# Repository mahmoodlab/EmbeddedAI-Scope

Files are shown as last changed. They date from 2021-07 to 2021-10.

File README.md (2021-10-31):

# Embedded AI Scope

*A 3D printed embedded AI-based microscope for pathology diagnosis.*

© This code is made available for non-commercial academic purposes.

*TL;DR: We present a 3D printed microscope coupled with a tiny embedded AI processor for running deep models trained on whole slide images. Tested on lung cancer and head and neck cancer detection and subtyping for both FFPE slides and frozen sections. The proposed setup can be used in low resouce settings where expensive slide scanners, computing equipment and pathology expertise may not be available. The setup can also be used for immidiate diagnosis from frozen sections during surgery.*

### Requirements

The setup of this device requires two small single-board computers (ideally one of which should be specialized for deep learning, such as an Nvidia Jetson Nano). 
Current STLs support an Nvidia Jetson Nano for model inference and a Raspberry Pi for imaging processing. A Raspberry Pi Camera V2 is used for imaging of samples. The STLs support a battery pack at most as large as the Jetson Nano and a 7 inch touch screen, though the specific dimensions of the variable STLs could be changed to accommodate for different setups (for example a larger screen, larger battery packs, or more than one battery pack). 

### Instructions

STL files for 3D printing are in `/stls`. The prints have been tested using a stereolithography (SLA) 3D printer. It is important to note that the battery pack(s) and screen are not specific to the design, as a wide variety of models and parts would provide the necessary functionality. Consequently, the 3D printed parts that house these components would need to be variable and easily modified to fit specific parts, so we include the scripts that generate these parts for customization. See [here](stls/housing_scripts/modifying_housing_stls.md) for details on modifying these STLs.

To build the device,

* Please see [here](stls/assembly_instructions.pdf) for a list of parts and specific assembly instructions with pictures. 
* Also see [assembly video](https://drive.google.com/file/d/1WPFa4IFCZg4AjeARS-ab-TACosYXbkmb/view?usp=sharing) for a very general overview and timelapse of assembly. 
* Ethernet file transfer (if needed) between the Jetson Nano and the Raspberry Pi can be set up in many ways. See [here](stls/ethernet_instructions.md): for details.
* After assembling and setting up the Ethernet connection (if needed), please see [model instructions](docs/README.md) for installing requirements and a toy example.

High-level overview of device structure and setup:

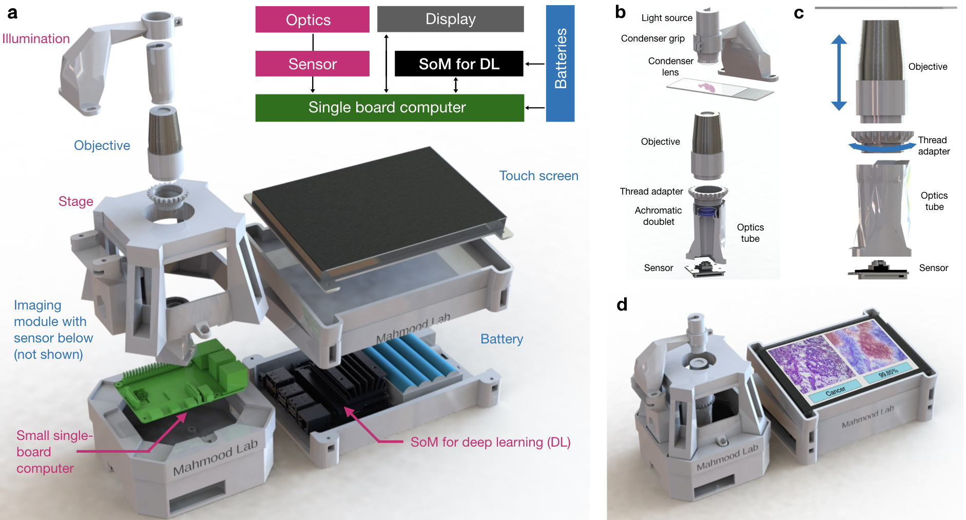
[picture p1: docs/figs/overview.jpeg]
Overview of device


Comparison with traditional development and deployment setups:

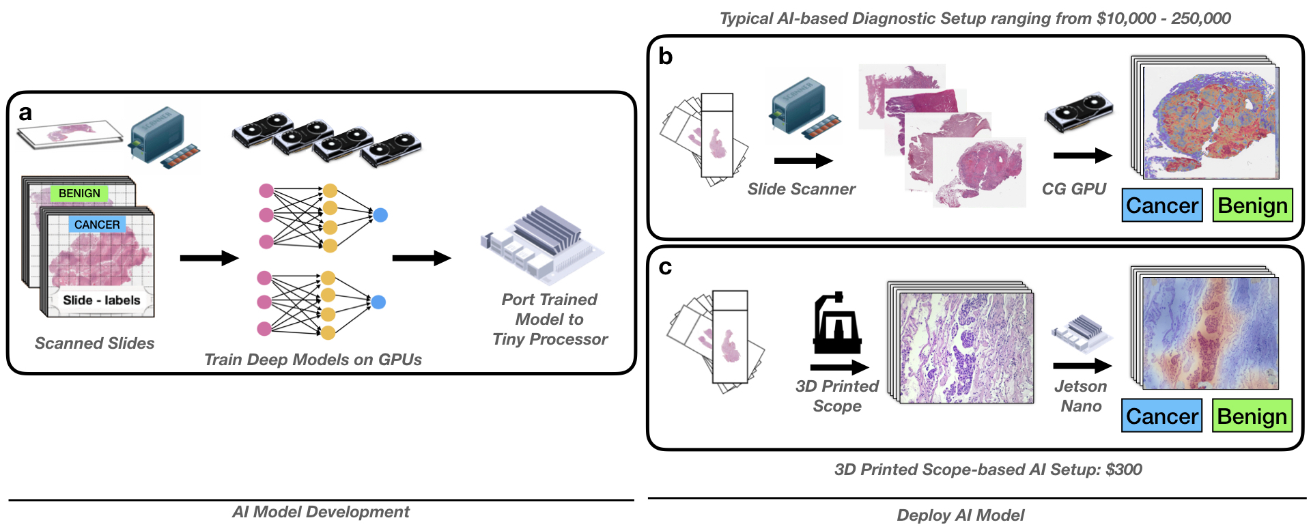
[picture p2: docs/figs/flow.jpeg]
Pipeline flow


### Acknowledgments
[CLAM](https://github.com/mahmoodlab/CLAM) and [OpenFlexture](https://github.com/rwb27/openflexure_microscope)

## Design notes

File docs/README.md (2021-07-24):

### TOY Example
First download [data](https://drive.google.com/drive/folders/1ofAFtL0PJd7fewOs3b44ejUzM-FwyQk0?usp=sharing) and put the data folder bwh_lung_2652 inside **phone_clam/data/**

See [here](INSTALLATION.md) for installation.

To run example:
``` shell
CUDA_VISIBLE_DEVICES=0 python infer_and_interpret.py --config_file heatmap_config_test.yaml --overlap 0.5
```

Generated heatmaps will be saved under **heatmaps/heatmap_production_results**.
Inferred results will be saved under **heatmaps/results**.
Settings can be modified using .yaml config files stored under **heatmaps/configs**; the config file corresponding the toy example is **heatmap_config_test.yaml** and is passed to the inference script via --config_file

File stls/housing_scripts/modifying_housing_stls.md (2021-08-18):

### Modifying STLs for screen, battery, and Jetson housing

The default design consists of a microscope component and a separate deep learning component. The microscope STLs are fixed due to specific dimensions (such as focal lengths and tube lengths) to achieve the desired magnification. However, the deep learning component also houses a touch screen and battery packs, which are up to a high degree of customization specific to a build (such as using different sized battery packs and screens with different dimensions). 

To address this, we provide the openSCAD scripts that generate the STLs and made it modular and easy to customize so that the STLs can be adapted to these highly variable parts.

#### Using openSCAD

The scripts are located in `lcd_and_board.scad`. These scripts generate both the top and bottom half of the housing component. See the comments in the script for details.

#### Other options

Aside from directly modifying openSCAD, these parts were designed with relatively simple transforms in mind so that it is recognizable by CAD software, such as using the Recognize Features function of FeatureWorks as part of SolidWorks).

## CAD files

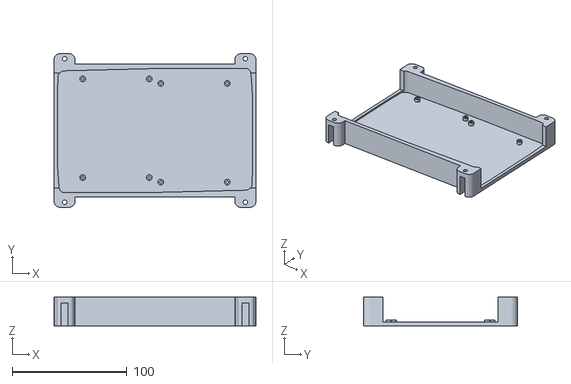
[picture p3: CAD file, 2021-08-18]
stls/lcd_and_board_bottom_part.stl
176.0 x 134.0 x 25.0

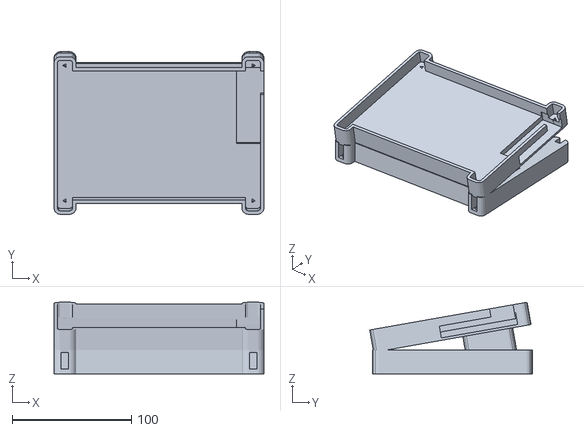
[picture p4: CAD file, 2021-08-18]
stls/lcd_and_board_top_part.stl
176.0 x 136.3 x 60.0

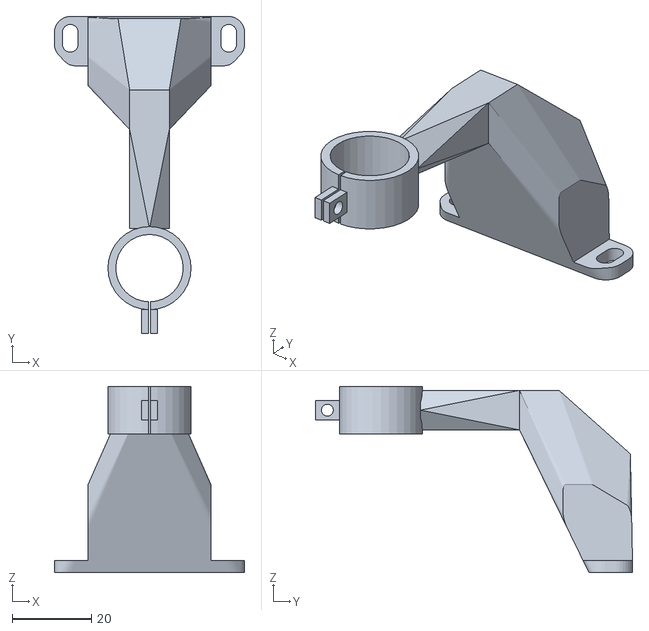
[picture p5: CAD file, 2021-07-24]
stls/condenser_mount.stl
48.0 x 80.0 x 47.0

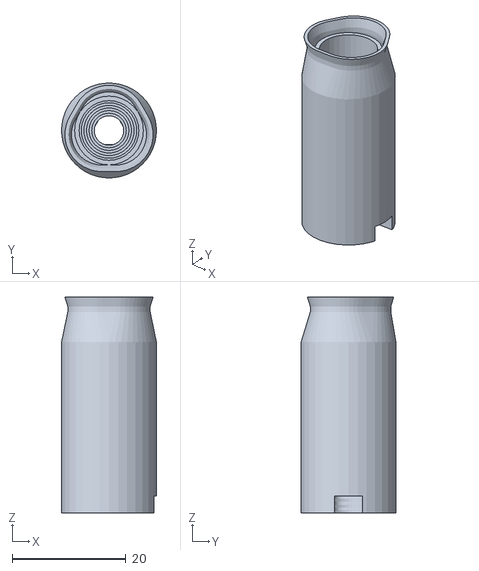
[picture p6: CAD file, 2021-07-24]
stls/condenser.stl
16.7 x 16.7 x 38.0

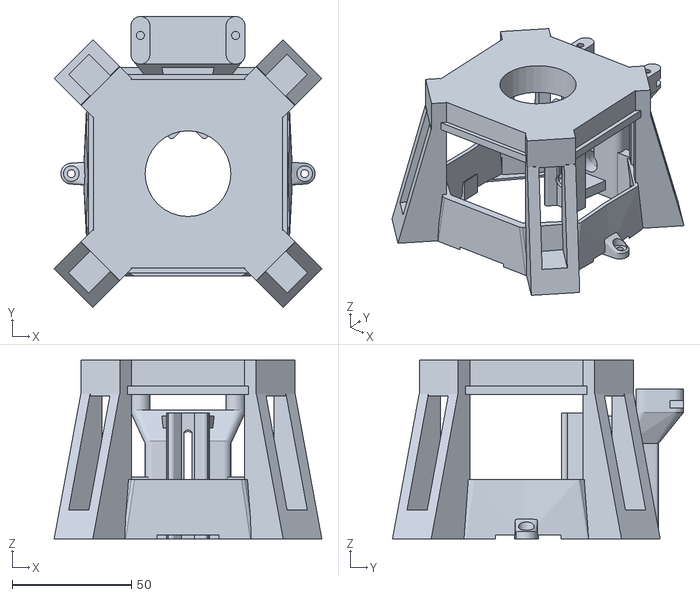
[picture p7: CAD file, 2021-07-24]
stls/stage.stl
112.4 x 122.2 x 75.0

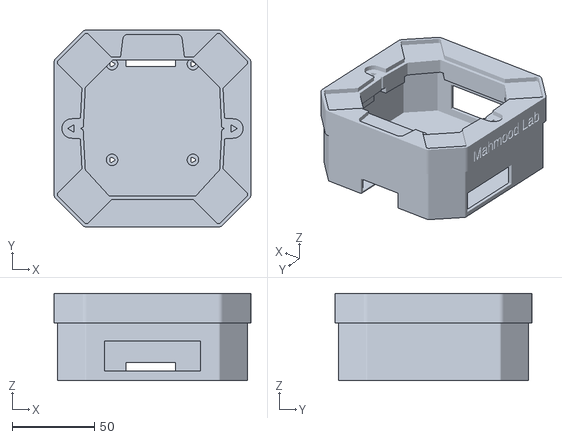
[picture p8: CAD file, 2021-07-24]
stls/microscope_stand.stl
119.4 x 119.4 x 53.0

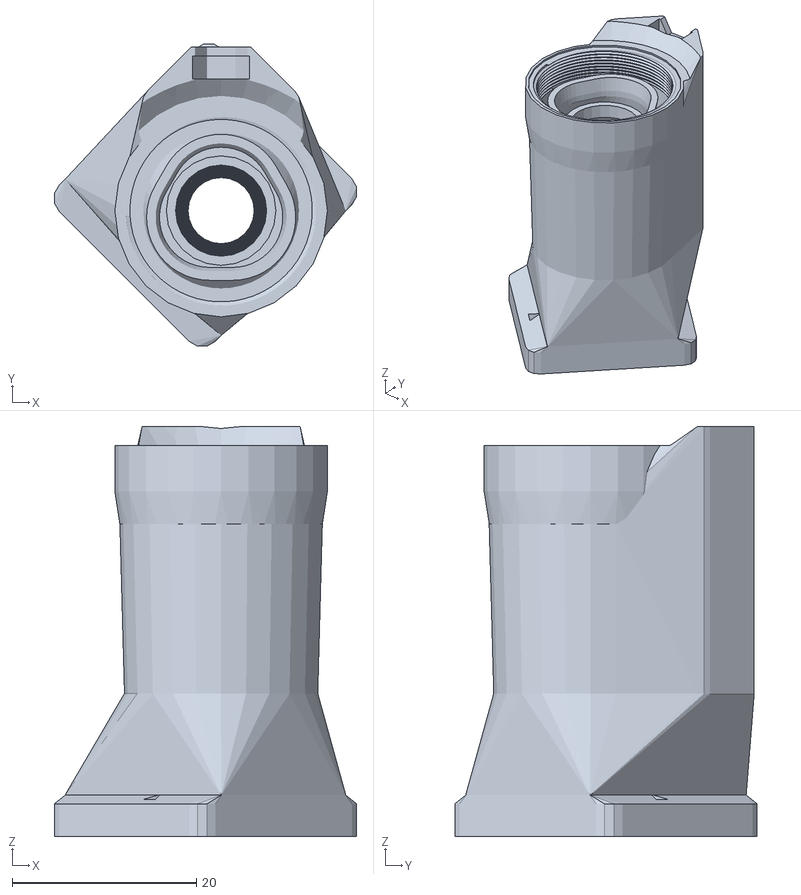
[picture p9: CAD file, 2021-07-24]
stls/optics_thread_tube.stl
32.9 x 32.9 x 44.5

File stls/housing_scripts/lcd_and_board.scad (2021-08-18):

eps = 0.05; // tolerance value 
screen_dims = [166, 106, 12]; // x,y,z dimensions of screen in milimeters, depends on screen
screw_port_dims = [8.5, 9, screen_dims.z]; // x,y,z dimensions of screen screw holes relative to the corner of the screen, depends on screen
board_dims = [];
board_pos1 = [-63,45,5];
board_pos2 = [63,-45,5];

/**
Note that base_height needs to be greater than height of Jetson and height of battery pack(s).
**/
base_height = 45; // Height of base of top housing component measured from bottom
bottom_height = 25; // Height of bottom housing component

// LCD casing is rotated to give a 10 degree slant
LCD_slant = 10;

// Positions of LCD ports to hollow out later
module lcd_screw_ports(screen = screen_dims, screw = screw_port_dims) {
    translate([screen.x/2-screw.x, screen.y/2, 0]) cube(screw_port_dims);
    mirror([1,0,0]) translate([screen.x/2-screw.x, screen.y/2, 0]) cube(screw_port_dims);
}

// Basic structure of screen to hollow out space later
module screen(screen = screen_dims) {
    translate([-screen.x/2, -screen.y/2, 0]) cube(screen);
}

// Make a 2D footprint of the basic LCD screen structure used to offset and extrude later to form outer structure of LCD housing
module lcd_footprint(screen = screen_dims, screw = screw_port_dims) {
    offset(2) projection() union() {
        lcd_screw_ports();
        mirror([0,1,0]) lcd_screw_ports();
        translate([-screen.x/2, -screen.y/2, 0]) cube(screen);
    }
}

// Space for LCD body, depends on screen
module lcd_hollow(screen = screen_dims, screw = screw_port_dims) {
    linear_extrude(height = screen_dims.z) lcd_footprint();
}

// Space for wiring to LCD, depends on screen
module lcd_wiring_hollow(screen = screen_dims, screw = screw_port_dims) {
    lcd_wiring_space = [20+3,65,10]; // Dimension of space to be hollowed, depends on screen and wires
    wiring_z_offset = 17; // Z offset for wiring to give extra space
    // Horizontal opening on the right side for wiring
    translate([screen.x/2-lcd_wiring_space.x+5+eps,-screw.y,screen.z-wiring_z_offset]) cube(lcd_wiring_space);
    // Extra space for bulkier HDMI cord
    translate([screen.x/2+eps,screen.y/2-2*screw.y,screen.z-wiring_z_offset]) cube([5,20,wiring_z_offset]);
}

// Outer structure of LCD housing
module lcd_casing_structure() {
    linear_extrude(height = screen_dims.z + 7) offset(3) lcd_footprint();
}

// Screw holes to secure LCD
module lcd_screw_holes(screen = screen_dims, screw = screw_port_dims) {
    // Holes are defined as with the cylinder function with $fn as 3 so that they are essentially triangular
    lcd_hole_d = 4; // Diameter of LCD screw hole, depends on size of screw used 
    module screw_hole(screen = screen_dims, screw = screw_port_dims) {
        translate([screen_dims.x/2-screw.x/2,screen_dims.y/2+screw.y/2,2]) cylinder(999, d = lcd_hole_d, $fn = 3);
        mirror([1,0,0]) translate([screen_dims.x/2-screw.x/2,screen_dims.y/2+screw.y/2,2]) cylinder(999, d = lcd_hole_d, $fn = 3);
    }
    screw_hole();
    mirror([0,1,0]) screw_hole();
}

// LCD housing to be rotated
module lcd_casing_top() {
    difference() {
        // Outer structure shell for LCD housing
        lcd_casing_structure();
        // Hollow out space for LCD, wiring, and screw ports 
        union() {
            translate([0,0,7+eps]) lcd_hollow();
            translate([0,0,7+eps]) lcd_wiring_hollow();
            lcd_screw_holes();
        }
    }
}

// Rotated LCD housing
module lcd_casing(screen = screen_dims, screw = screw_port_dims) {
    // Rotated to give a slant for ease of usage 
    translate([0,0,(screen.y+2*screw.y+10)*sin(LCD_slant)/2]) rotate(LCD_slant, [1,0,0]) lcd_casing_top();
}

// Two legs to support slanted LCD housing
module lcd_support(screen = screen_dims, screw = screw_port_dims, column_pos = 60) {
    // Make one of the legs
    module lcd_support_column(screen = screen, screw = screw) {
        /**
        The supports are essentially two cylinders hulled together, so support_dims_back and support_dims_front gives the dimensions of the taller and shorter cylinders respectively
        Note these are defined relative to screen and screw ports (this can be changed)
        **/
        support_dims_back = [10,5,(screen.y+2*screw.y+10)*tan(LCD_slant)+1];
        support_dims_front = [10,5,(screen.y+2*screw.y+10)*tan(LCD_slant)/3*2+1];
        // Hull the cylinders together to form the column
        hull() {
            translate([0,(screen.y+2*screw.y+10)*cos(LCD_slant)/2*0.25,-2]) rotate(LCD_slant,[1,0,0]) cylinder(h = support_dims_front.z, r = support_dims_front.y);
            translate([0,(screen.y+2*screw.y+10)*cos(LCD_slant)/2*0.75,-2]) rotate(LCD_slant,[1,0,0]) cylinder(h = support_dims_back.z, r = support_dims_back.y);
        }
    }
    // Make both legs
    leg_pos = 60; // Position of legs
    translate([leg_pos,0,0]) lcd_support_column();
    translate([-leg_pos,0,0]) lcd_support_column();
}

// LCD housing and support 
module lcd_full(screen = screen_dims, screw = screw_port_dims) {
    lcd_casing();
    lcd_support(screen = screen_dims, screw = screw_port_dims);
}

// Model of Jetson Nano used to hollow out space later, quick and easy way to get dimensions and hole positions (could also use cube() or an STL of a different board if needed)
module jetson_space() {
    // Credit to https://grabcad.com/library/jetson-nano-3
    import("./libs/jetson_nano.stl");
}

// The battery pack used in the default setup was originally built as a HAT for Jetosn Nano, so it has the same dimensions and screw hole positions, thus we just repeat the same dimensions and positions twice
module boards(board_pos1, board_pos2) {
    hull() {
        // Change one of these to desired dimensions for custom battery pack(s), leave the other one for Jetson Nano
        translate(board_pos1) rotate(-90, [0,0,1]) jetson_space();
        translate(board_pos2) rotate(90, [0,0,1]) jetson_space();
    }
}

// Hollow out space for board wiring and cords
module board_wiring_cutouts() {
    translate([0,0,15]) cube([999,100,23], center = true);
}

// Hollow out holes for bolt
module hole(screen = screen_dims, screw = screw_port_dims, hole_z, hole_d) {
    translate([screen.x/2-screw.x/2, screen.y/2+screw.y/2+5,hole_z+eps]) cylinder(22, d = hole_d, $fn=25);
}
    
module bottom_base_screw(screen = screen_dims, screw = screw_port_dims) {
    // Define rectangular slot for ease of access to secure bolt and nut
    module slot(screen = screen, screw = screw) { 
        slot_dims = [6,10,base_height-bottom_height];
        translate([screen.x/2-screw.x+slot_dims.x/4,screen.y/2+screw.y/2-slot_dims.y/4+4,-eps]) cube(slot_dims);
    }
    bottom_base_hole_d = 4; // Diameter of hole for bolt
    bottom_base_hole_z = 5; // Height of hole for bolt to hollow out
    // Form slot and holes and reflect to make all four
    union() {
        hole(hole_z = bottom_base_hole_z, hole_d = bottom_base_hole_d);
        slot();
        mirror([1,0,0]) slot();
        mirror([1,0,0]) hole(hole_z = bottom_base_hole_z, hole_d = bottom_base_hole_d);
    }
    mirror([0,1,0]) union() {
        hole(hole_z = bottom_base_hole_z, hole_d = bottom_base_hole_d);
        slot();
        mirror([1,0,0]) slot();
        mirror([1,0,0]) hole(hole_z = bottom_base_hole_z, hole_d = bottom_base_hole_d);
    }
}

// Screw holes to connect top_base and bottom_base together
module top_base_screw(screen = screen_dims, screw = screw_port_dims) {
    top_base_hole_d = 4; // Diameter of hole for bolt
    top_base_hole_z = 15; // Height of hole for bolt to hollow out
    union() {
        hole(hole_z = top_base_hole_z, hole_d = top_base_hole_d);
        mirror([1,0,0]) hole(hole_z = top_base_hole_z, hole_d = top_base_hole_d);
    }
    mirror([0,1,0]) union() {
        hole(hole_z = top_base_hole_z, hole_d = top_base_hole_d);
        mirror([1,0,0]) hole(hole_z = top_base_hole_z, hole_d = top_base_hole_d);
    }
    /**
    Hollow out space for nut, use same dimensions as the space for the bottom base.
    This can be concealed better to improve aesthetics but we chose to keep it exposed for flexibility of bolt lengths and nut sizes
    **/
    translate([0,0,29]) linear_extrude(16+eps) projection() bottom_base_screw();
}
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

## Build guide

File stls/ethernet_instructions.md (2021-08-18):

### Setting up wired Ethernet connection 

If used in conditions without wireless Internet connection, the Raspberry Pi imaging component can communicate with the Jetson Nano deep learning component using wired Ethernet. There are a wide variety of ways to achieve this, such as using a combination of `inotifywait`, `watch`, and `scp`.

First, set a static IP for Jetson Nano

* Open `/etc/default/networking`
* Set `CONFIGURE_INTERFACES=no` to skip interface configuration on boot
* Open `/etc/network/interfaces`
* Modifying the following settings:

```
auto eth0
iface eth0 inet static
	address XXX.XXX.X.X
	netmask XXX.XXX.X.X
	gateway XXX.XXX.X.X
```

* Reboot and check with `ifup eth0`

Next, set a static IP for Raspberry Pi 

* Open `/etc/dhcpcd.conf`
* Scroll to the bottom of the file and add the following:

```
interface eth0
static ip_address=XXX.XXX.X.X
static routers=XXX.XXX.X.X
static domain_name_servers=XXX.XXX.X.X
```

* Reboot

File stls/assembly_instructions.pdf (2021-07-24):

Supplement - Assembly Instructions

Parts list
- Printed parts
- Computing hardware
- NVIDIA Jetson Nano
- Raspberry Pi 4
- Imaging and optics components
- Raspberry Pi Camera Module V2
- Achromatic doublet (12.7 mm diameter, 50 mm focal length)
- Condenser lens (12.7 mm diameter, 8 mm focal length)
- Finite conjugate microscope objective with RMS threads (20x used in images below)
- LED parts (not shown in image below)
- 5 mm white LED
- 330Ω resistor
- Electric wire (with female socket header for GPIO pin connection. Note that all LED parts can be purchased in a basic LED kit.)
- Tape
- Nuts and bolts (not shown in image below)
- 2 M2 screws
- 8 to 16 M2.5 screws
- 6 M3 nuts
- 2 M3 x 8 mm screws
- 1 M3 x 10 mm screw
- 4 M3 x 12 mm screws

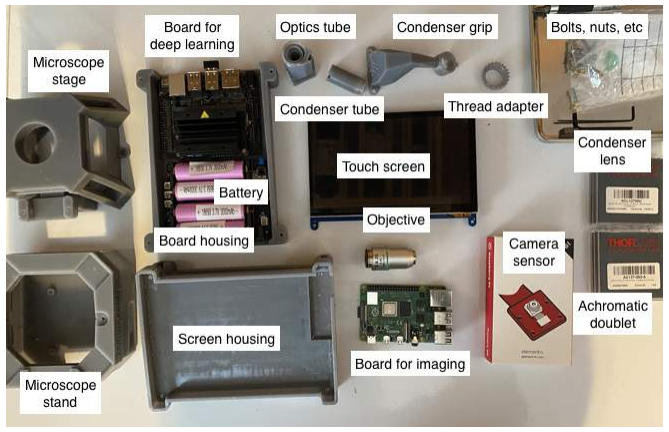
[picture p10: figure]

Assembling the optics components
1. Push the achromatic doublet into the optics tube, with the less convex side facing into the tube (make sure that the doublet is as flat as possible in the slot). See right below for the cross section view (doublet shown in blue).

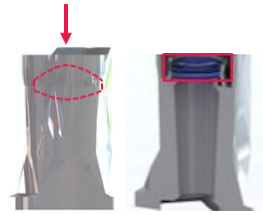
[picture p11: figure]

2. Insert an M3 nut into the slot at the top, then twist an M3 x 10 mm screw into the nut (note that there will be intended empty space between the screw cap and the optics tube).

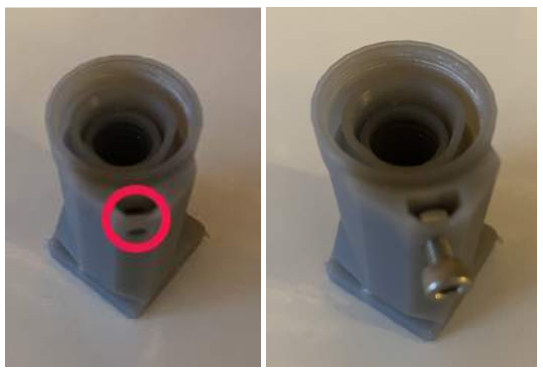
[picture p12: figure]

3. Twist and remove the built-in lens of the sensor. Take extra precaution to prevent dust from gathering on the sensor surface.

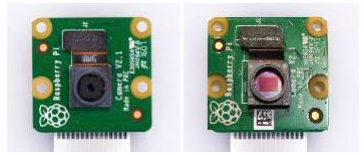
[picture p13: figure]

### 4. Fix the sensor to the bottom of the optics tube using 2 M2 x 6 mm screws

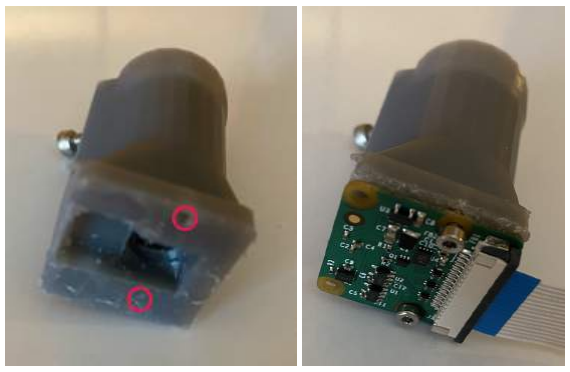
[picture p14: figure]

### 5. Push the condenser lens into the condenser tube

### 6. Connect the objective lens with the thread adapter

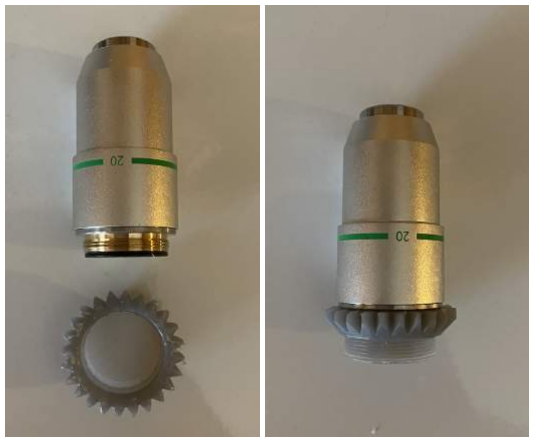
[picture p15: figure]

### 7. Connect the thread adapter with the optics tube

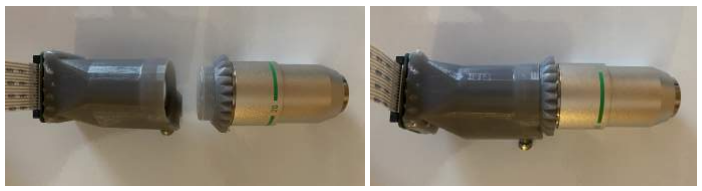
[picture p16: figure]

8. Wire the LED according to the schematic below (GPIO wiring shown here for completeness. Connect to Raspberry Pi GPIO pins in step 5 of the next part).

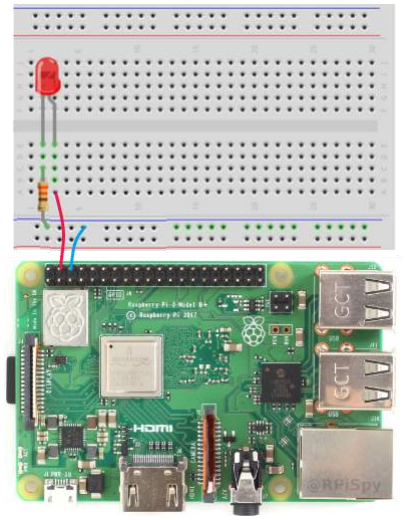
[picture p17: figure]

Assembling the microscope body
1. Fix the optics tube to the stage by inserting the screw cap into the slot opening (left image below) and move the optics tube upward (center image). Tighten the screw at a desired height through the opening slot (right image) according to the working distance of the optics system.

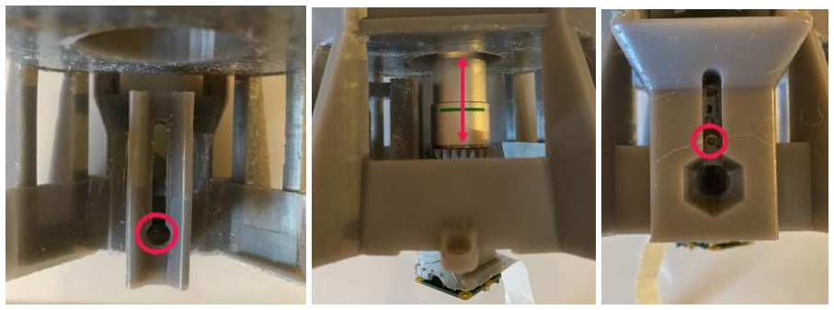
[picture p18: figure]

2. Fix the Raspberry Pi to the bottom of the stand using 2 to 4 M2.5 screws.

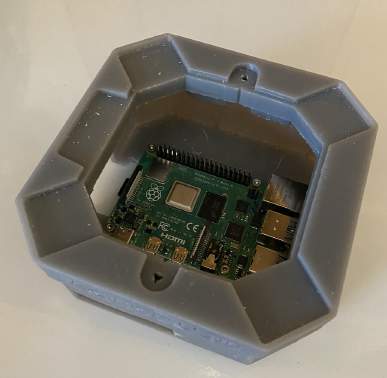
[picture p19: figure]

3. Place a nut in each of the 2 slots below the screw holes for the condenser grip on the stage. Screw the condenser grip to the body using 2 M3 screws.

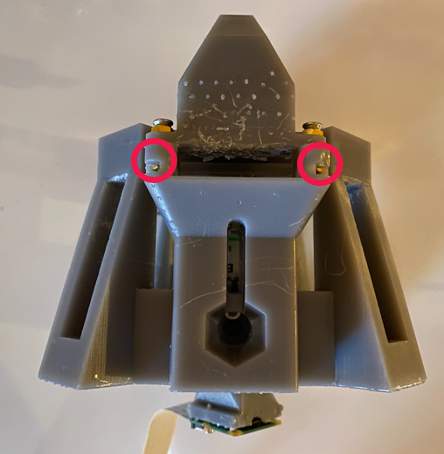
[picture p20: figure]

4. Place the condenser tube in the condenser grip. Use an M2 screw to tighten the clamp if needed.

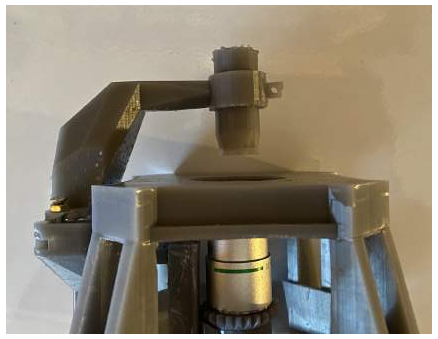
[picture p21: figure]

5. Connect the LED wires with the GPIO pins of the Raspberry Pi accordingly (Use GPIO 4 for 5V power and GPIO 6 for ground. See green box in the schematic below).

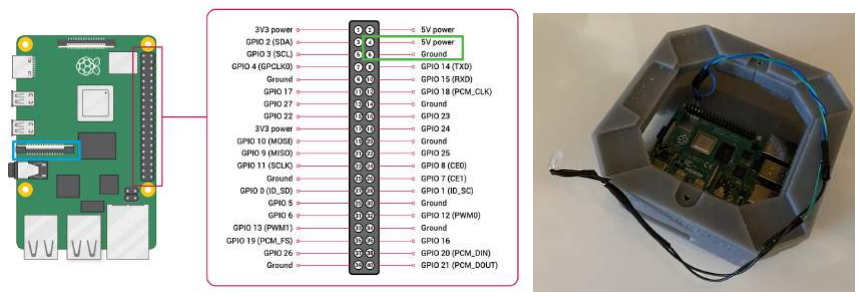
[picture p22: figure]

6. Tape the LED to a slot at the top end of the condenser tube (you can thread the wire through the space between the stage and the condenser grip to minimize exposed wires). Connect the camera to the camera connector of the Raspberry Pi (blue box in the schematic above). Screw the stage and the stand together using 2 M3 screws.

Assembling the deep learning components

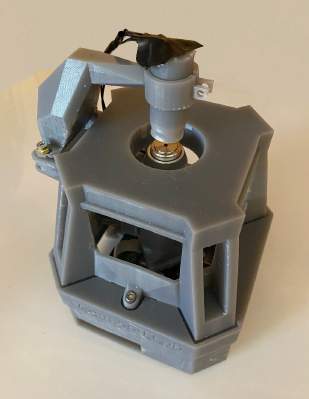
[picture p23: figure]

1. Fix the Jetson Nano and battery pack to the bottom of the board housing using 4 to 8 M2.5 screws

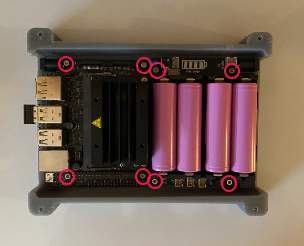
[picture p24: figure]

2. Insert an M3 nut into each slot at the bottom half. Place and align the top half on top and screw together with 4 M3 x 12 mm screws.

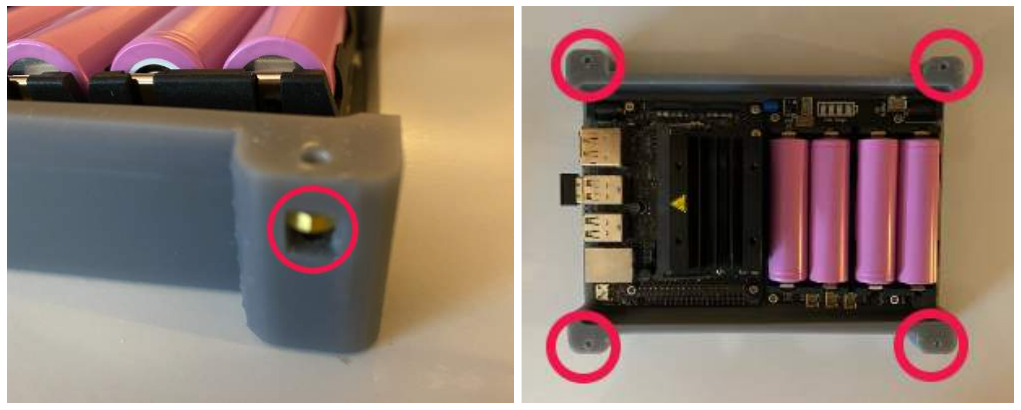
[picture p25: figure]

3. Fix the touch screen to the top of the board housing using 2 to 4 M2.5 screws. Wire the hardware accordingly and assembly is now finished.

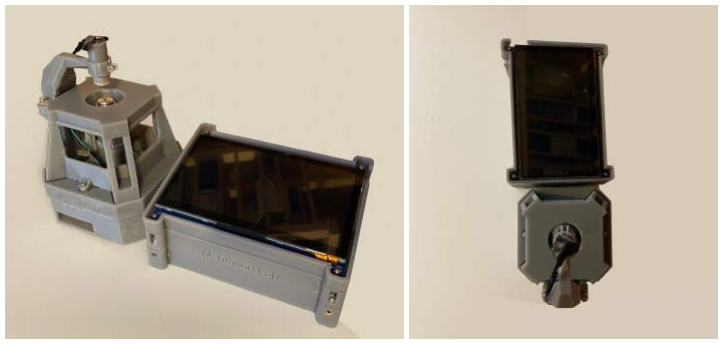
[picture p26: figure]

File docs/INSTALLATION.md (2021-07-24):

CLAM Installation Guide
===========
For instructions on installing anaconda on your machine (download the distribution that comes with python 3):
https://www.anaconda.com/distribution/

After setting up anaconda, first install openslide:
```shell
sudo apt-get install openslide-tools
```

Next, use the environment configuration file located in **docs/clam.yaml** to create a conda environment:
```shell
conda env create -n clam -f docs/clam.yaml
```

Activate the environment:
```shell
conda activate clam
```

Once inside the created environment, to install smooth-topk (first cd to a location that is outside the project folder and is suitable for cloning new git repositories):

```shell
git clone https://github.com/oval-group/smooth-topk.git
cd smooth-topk
python setup.py install
```

When done running experiments, to deactivate the environment:
```shell
conda deactivate clam
```
Please report any issues in the public forum.

[Return to main page.](README.md)

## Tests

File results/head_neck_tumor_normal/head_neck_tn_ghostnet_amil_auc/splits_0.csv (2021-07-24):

 | train | val | test
0 | C3L-00995-27 | C3N-00825-23 | C3N-03876-23
1 | C3N-01758-24 | C3N-03841-22 | C3N-03045-22
2 | C3N-03889-21 | C3L-00977-22 | C3N-01948-21
3 | C3N-00498-23 | C3N-01859-24 | C3L-04025-25
4 | C3N-03933-23 | C3N-04279-21 | C3N-00871-25
5 | C3N-03783-21 | C3L-04844-23 | C3N-01948-23
6 | C3L-02651-22 | C3N-03619-21 | C3N-03045-21
7 | C3N-00846-21 | C3N-01756-21 | C3N-02694-22
8 | C3N-01858-22 | C3L-04844-21 | C3N-00204-22
9 | C3N-01338-21 | C3N-02713-26 | C3N-02700-21
10 | C3N-03490-23 | C3N-00825-24 | C3N-00204-24
11 | C3N-02279-21 | C3N-02275-24 | C3N-00871-22
12 | C3L-02621-21 | C3N-02713-21 | C3N-03876-22
13 | C3N-01620-23 | C3N-01756-25 | C3N-00204-26
14 | C3N-01754-25 | C3N-04273-21 | C3L-04025-27
15 | C3L-00987-22 | C3N-01859-21 | C3N-00204-27
16 | C3N-00828-21 | C3L-00977-26 | C3L-01237-24
17 | C3N-00846-26 | C3N-03619-22 | C3L-04025-23
18 | C3L-04791-27 | C3N-04273-23 | C3N-00822-22
19 | C3N-04153-21 | C3N-04279-25 | C3N-02700-22
20 | C3N-03009-23 | C3N-03841-21 | C3L-04025-21
21 | C3N-01645-25 | C3N-00825-25 | C3N-00204-23
22 | C3N-00498-24 | C3N-03841-23 | C3N-01948-24
23 | C3N-00519-25 | C3L-04844-22 | C3N-04280-23
24 | C3L-00994-21 | C3N-02713-23 | C3L-04025-28
25 | C3N-04611-23 | C3N-02713-22 | C3N-00204-21
26 | C3N-03849-21 | C3N-03619-26 | C3N-00822-21
27 | C3N-00295-23 | C3N-02275-23 | C3L-04025-24
28 | C3N-03878-23 | C3N-03619-23 | C3N-03876-21
29 | C3N-03888-23 | TCGA-CV-7438-01Z-00-DX1.DE00CAA6-5750-4231-A2D3-7F8CF789E512 | C3L-04025-22
30 | C3N-03888-21 | TCGA-BB-A5HY-01Z-00-DX1.0BDC44E8-17E5-4907-9C9B-417FF335AEC8 | C3L-01237-26
31 | C3L-04354-23 | TCGA-BB-4228-01Z-00-DX1.170b1b9a-05ac-4115-965e-56c2af944f1f | C3N-03457-22
32 | C3N-03612-23 | TCGA-CV-7414-01Z-00-DX1.B821209A-8EA4-4BA1-AEEC-8E2E330763D4 | C3N-02700-26
33 | C3N-02925-23 | TCGA-BB-7861-01Z-00-DX1.efdd186f-1bbf-4e43-9875-9458cebcd0dd | C3N-02694-23
34 | C3N-00846-23 | TCGA-H7-A6C4-01Z-00-DX1.0A41FEF9-3604-4982-BEFB-2438861C62D4 | C3N-02700-23
35 | C3N-03042-21 | TCGA-CV-7183-01Z-00-DX1.B90BA26B-F922-4C10-BCA4-203E1453D4B3 | C3N-00871-21
36 | C3N-01754-21 | TCGA-CV-A461-01Z-00-DX1.D594E898-5EF0-4C56-A1B8-942DB81F54C5 | TCGA-CN-A642-01Z-00-DX1.74FF21F1-93CA-41A9-A652-3435B0EFDAD5
37 | C3N-03028-21 | TCGA-IQ-A6SG-01Z-00-DX1.3A03D675-BE6D-49E5-9FC2-B0E4CE967D09 | TCGA-CQ-7071-01Z-00-DX1.AEFEDFCA-0D2F-42AE-8D3F-8D9DD42F5E2D
38 | C3N-03012-21 | TCGA-CX-7219-01Z-00-DX1.281050F5-06AE-497D-8153-355FB7E8076D | TCGA-CN-A63W-01Z-00-DX1.57F5E8BA-E352-4AC9-A800-21DF745474B8
39 | C3N-03487-26 | TCGA-CQ-7065-01Z-00-DX1.083ed2a3-9074-4e48-b950-7255ca54ce77 | TCGA-CN-6017-01Z-00-DX1.690fa1af-4b51-41c8-a52d-bd1341f990e9
40 | C3N-04275-25 | TCGA-CN-6988-01Z-00-DX1.1fc4c572-3495-4f5a-9f1a-60c04096d188 | TCGA-BA-6873-01Z-00-DX1.F0A84DE2-7A08-44D5-9FD1-A284F55AA8C1
41 | C3N-03781-21 | TCGA-CV-6961-01Z-00-DX1.325AA036-BCD6-450E-96B2-1317C4DB2412 | TCGA-QK-A64Z-01Z-00-DX1.A894D5AB-8914-412A-B719-E4ED659C8D88
42 | C3N-03433-22 | TCGA-BB-A6UM-01Z-00-DX1.403D4D0A-83F4-4D2F-9CBB-C7A1470AC565 | TCGA-QK-A64Z-01Z-00-DX2.96E8ABB3-3925-402B-8E51-7CF8CA0C63B9
43 | C3L-04354-22 | TCGA-CQ-A4CB-01Z-00-DX1.5761AA04-B8D3-4DD6-B20E-55F940BC7019 | TCGA-CX-A4AQ-01Z-00-DX1.31ECF3F8-7BAF-4395-8163-DAC2BE88CE06
44 | C3N-03042-23 | TCGA-CV-A45Q-01Z-00-DX1.E14F6011-AB2C-4B4F-840B-83972A00C71F | TCGA-CV-A6JE-01Z-00-DX1.20137D17-19B3-49FF-9C3D-60933157E409
45 | C3N-03027-21 | TCGA-CV-6936-01Z-00-DX1.3065C974-E4DF-4BEF-9300-9E400E4513CB | TCGA-CQ-A4C6-01Z-00-DX1.98BDE0C7-81D1-410C-A0AD-1CD98F7DFD87
46 | C3N-01755-21 | TCGA-CV-6951-01Z-00-DX1.3C450DCF-B884-4C57-A60F-23D8C3F94CAF | TCGA-DQ-5629-01Z-00-DX1.A5FB326B-4EC1-4446-B98A-392126168863
47 | C3N-03837-21 | TCGA-CN-5365-01Z-00-DX1.26a33bd0-1eb3-4774-8be6-bf8501f4a9f9 | TCGA-CV-A45Y-01Z-00-DX1.14FF40A6-2D41-418A-B908-6095ABF7FD13
48 | C3N-02695-22 | TCGA-CN-4735-01Z-00-DX1.b7d37666-bd65-4d3b-826b-97e560444956 | TCGA-UF-A71D-01Z-00-DX1.4372D70E-9EF5-444D-AA78-A64FE53519BF
49 | C3L-02617-23 | TCGA-CQ-5333-01Z-00-DX1.f2c97975-dd7d-4dc9-a1b9-1528184cb8ad | TCGA-DQ-7588-01Z-00-DX1.1D1253F5-7C5A-46B4-B796-7DE7ED828080
50 | C3L-00987-27 | TCGA-DQ-5631-01Z-00-DX1.D9B0F531-4FE9-4D96-BE74-656B2F87F922 | TCGA-UF-A7JJ-01Z-00-DX1.C540BC43-FCAB-45DC-86BD-081CAE47A018
51 | C3N-01945-24 | TCGA-MZ-A6I9-01Z-00-DX1.478C5347-BF30-4CAA-8215-58778D79E33B | TCGA-KU-A66S-01Z-00-DX1.195F55BC-4F8F-4039-8E12-4B18C53A8B04
52 | C3N-00857-21 | TCGA-CN-4723-01Z-00-DX1.13483e7b-9322-4d39-8cd6-91e898bf2ee9 | TCGA-CV-A45Z-01Z-00-DX1.BAA8DD77-82AE-4441-ADDD-F41FF3476FEB
53 | C3N-02727-22 | TCGA-MT-A51X-01Z-00-DX1.A7469A54-DDD5-4B3E-A437-F51FBDD8B158 | TCGA-QK-A64Z-01Z-00-DX3.4C6D6F13-08E5-41DD-BE8F-D89087D00F22
54 | C3L-02621-28 | TCGA-CV-A6JY-01Z-00-DX1.0326449A-DADA-43C5-8B2C-1B3C662A3D7A | TCGA-IQ-A61I-01Z-00-DX1.6A796222-C609-472B-A905-C5D0521625D9
55 | C3L-00987-21 | TCGA-CV-5978-01Z-00-DX1.E2AD0A66-3A25-467F-8768-C0FC34844C79 | TCGA-CV-7421-01Z-00-DX1.297CD6B5-F3FB-446D-B505-094EEC1AB76A
56 | C3N-04611-26 | TCGA-P3-A6SX-01Z-00-DX1.AB3C5814-D645-4ED3-B81D-683E9FA0BBA5 | TCGA-CQ-A4CE-01Z-00-DX1.2E5A8284-C995-4B9F-9451-22DEC5EB2FB6
57 | C3L-00994-27 | TCGA-CV-7255-01Z-00-DX1.11D5B324-D223-4130-9CF1-1B138519A4A1 | TCGA-D6-A6EK-01Z-00-DX1.E2A056C2-ADEF-4800-86E9-1B95E5FB5F88
58 | C3N-03008-21 | TCGA-CV-7247-01Z-00-DX1.C4EA48AC-B844-4A4E-B2E4-31902F99FB7A | TCGA-CQ-7068-01Z-00-DX1.4a9d6c19-4f72-4d00-97fa-70f72cd4ec0f
59 | C3N-03612-22 | TCGA-HL-7533-01Z-00-DX1.5428d6cb-2417-4b51-9453-dd2c583bb395 | TCGA-CV-7245-01Z-00-DX1.9128EEC2-17DC-4DCA-8B91-508A0C0C52D2
60 | C3L-04849-23 | TCGA-CQ-A4C7-01Z-00-DX1.491FFBCB-ABD0-4D58-8CE7-A9E141A46DE5 | TCGA-BA-6872-01Z-00-DX1.F99F6394-D319-4599-B124-D2A6692FA096
61 | C3L-02617-21 | TCGA-QK-AA3J-01Z-00-DX1.ABCA519E-CF09-4FB3-812F-A977C4F0BA91 | TCGA-BA-A6DB-01Z-00-DX1.6EC4113A-D48B-4F83-84EF-1A811C67FDFE
62 | C3N-03012-25 | TCGA-CN-6989-01Z-00-DX1.dd68e391-1d00-4bfc-9be9-ff5024bea237 | TCGA-CV-5431-01Z-00-DX1.27F6CF96-195D-4811-97CC-B38A4FA80E06
63 | C3N-01858-25 | TCGA-CV-A6K0-01Z-00-DX1.C9946763-9EAE-477E-A605-905CE7E6C339 | TCGA-CV-6959-01Z-00-DX1.AEC54909-0A3A-43E2-966C-7410CD7488EF
64 | C3N-03612-26 | TCGA-CN-5359-01Z-00-DX1.30a19cad-c2b0-4c5f-bd5d-89aa8ac2bb91 | TCGA-T2-A6X2-01Z-00-DX1.8A72CC59-D322-4C0B-AD52-ACF91CC3B72F
65 | C3N-03011-21 | TCGA-CV-A6JN-01Z-00-DX1.49317AB4-850C-4A4B-B5EA-2C242B32E1DA | TCGA-T2-A6WX-01Z-00-DX1.E4C76787-98AE-439C-8021-9B7F4649601B
66 | C3N-02727-21 | TCGA-HD-A6HZ-01Z-00-DX1.DA05A854-E793-4CEA-A18D-0D5D2C0B4FE9 | TCGA-MT-A67A-01Z-00-DX1.7C12D59B-185E-4A25-B67F-A4ECEBE3746A
67 | C3N-01946-24 | TCGA-CV-7177-01Z-00-DX1.F904D98D-645B-4579-9757-28561DFEFB93 | TCGA-CV-6952-01Z-00-DX1.F3716B4F-DC4B-4AC0-9397-E93BFB5E7688
68 | C3N-00519-23 | TCGA-UF-A718-01Z-00-DX1.D7364E57-41D6-4865-B194-9448FF17E1EE | TCGA-HD-8635-01Z-00-DX1.3A830969-5E7F-422C-8753-E4AEFEAED6B8
69 | C3N-03620-21 | TCGA-CV-7433-01Z-00-DX1.2EA4930A-41AE-448A-A840-134A927B52EB | TCGA-P3-A6T2-01Z-00-DX1.693C40C7-0980-4426-B2D2-514AC727A302
70 | C3N-03226-26 | TCGA-CV-6433-01Z-00-DX1.069ACB4F-226C-40B6-A141-0E2A1788E68E | TCGA-CN-5358-01Z-00-DX1.6554cdc1-7d01-4310-a60a-79b8ed7a8679
71 | C3L-02617-27 | TCGA-CV-7423-01Z-00-DX1.B40488AA-9D45-4B58-993B-F4BF4F1ACEBF | TCGA-DQ-7591-01Z-00-DX1.8304B939-542C-4D30-8C77-F705DE1311FF
72 | C3N-03487-22 | TCGA-CV-6953-01Z-00-DX1.2CCF64F9-3DD2-493D-87A0-D9BB10D06FD7 | TCGA-CV-6956-01Z-00-DX1.EB7DE6CC-540E-4257-B596-80F310B93C81
73 | C3N-01947-22 | TCGA-P3-A5QA-01Z-00-DX1.4EA8DD62-AF4F-4872-B2AA-F40125D45D3A | TCGA-CV-7095-01Z-00-DX1.0D531563-9863-480D-9B60-1239E88A8D65
74 | C3N-03783-23 | TCGA-CV-5434-01Z-00-DX1.096C8215-F997-4FFD-A9F3-22A0324B5A01 | TCGA-CV-7263-01Z-00-DX1.F3BC8C3D-BD3B-4663-9C3B-251ECAA4414D
75 | C3L-02651-21 | TCGA-CV-7414-01A-01-TS1.d08e8e9e-3072-4b28-a611-f568dd516f25 | TCGA-BA-5556-01Z-00-DX1.6941a8fa-2f68-41d8-8661-82601570d901
76 | C3N-00306-23 | TCGA-CV-7433-01A-01-BS1.a1ae37ae-4715-4c92-9f8d-f03b39a3d7d0 | TCGA-P3-A6T4-01Z-00-DX1.5DC1C4B4-7BB2-44AE-8D7A-FFFA3CB4BE63
77 | C3N-01339-21 | TCGA-CV-A6JN-01A-01-TS1.0B9BC7D6-81C7-43AC-A110-EEF556442348 | TCGA-BA-6871-01Z-00-DX1.4d9ca329-f8d5-4c31-a20f-9d4fba728326
78 | C3N-02333-23 | TCGA-CV-5434-01A-01-TS1.4a6dffc4-b178-4a0a-924b-df0740273784 | TCGA-BA-5151-01Z-00-DX1.32EE476B-128D-4153-A57C-CFA823B993A2
79 | C3N-01757-23 | TCGA-CV-A461-01A-04-TS4.79E74477-1C7E-436B-A359-86C226F4A6FA | TCGA-IQ-A61H-01Z-00-DX1.EAB7367A-7283-4FEE-AE8E-9B81000C7C68
80 | C3N-01943-23 | TCGA-CV-6961-01A-01-BS1.efa67512-ca7b-4bfe-976e-deb9809ef1e2 | TCGA-BA-A6DL-01Z-00-DX1.A2E13153-88A9-411B-AA0F-56314E72E2CB
81 | C3N-00519-22 | TCGA-BB-4228-01A-01-BS1.a4a5c486-1b93-4b7a-9fb1-c1727f1f9388 | TCGA-CV-7235-01Z-00-DX1.4779177A-2956-41BC-8324-00729FEE8B9A
82 | C3L-00995-26 | TCGA-CN-6988-01A-01-BS1.32230035-2ea2-42a0-87b9-26ceb84c19eb | TCGA-UF-A7JA-01Z-00-DX1.4BA7AC34-0563-45C4-AAE1-E5CD224432ED
83 | C3N-03620-22 | TCGA-CN-6995-01A-02-BS2.19ad8574-4c68-4408-823c-2b36d4d6681e | TCGA-QK-A64Z-01Z-00-DX4.370068FC-E205-494A-A5C1-0CBAFE2A28F2
84 | C3N-02925-22 | TCGA-CV-6433-01A-01-BS1.8bf55120-74be-4723-8963-c53367ea1d74 | TCGA-CV-7440-01Z-00-DX1.ABC0027C-EBB2-4BDF-9AE7-116D4F38DD70
85 | C3N-00828-25 | TCGA-CV-5978-01A-01-BS1.fa2ff37a-e607-40f5-b76f-fba64819ecad | TCGA-DQ-5629-01A-01-TS1.da763f03-154f-4d0b-90cb-3193a5571abb
86 | C3N-00828-22 | TCGA-CQ-5333-01A-01-TS1.eab34d9c-2990-45ef-852f-f56ccc9b67d4 | TCGA-CV-7263-01A-01-BS1.d515863e-a8ee-4469-b086-7ae21a213496
87 | C3N-02333-21 | TCGA-CV-A45Q-01A-01-TS1.17189C18-86E2-4725-9F3A-B25350B73236 | TCGA-CQ-5327-01A-01-TS1.42ba9f70-89b5-4880-ad33-7607367c1350
88 | C3N-03226-23 | TCGA-CV-6936-01A-01-TS1.0b88906d-95de-4cf0-a643-4b730822b740 | TCGA-CN-5358-01A-01-TS1.40850e44-f18f-4ce8-ae0b-833dad79b5f3
89 | C3N-03782-21 | TCGA-UF-A718-01A-02-TSB.F3FE2F70-1E5B-49F9-8836-36A8E9A21435 | TCGA-CN-A63W-01A-01-TS1.650A0470-DDDB-42F1-9A9A-846161DA582B
90 | C3N-04152-22 | TCGA-H7-8501-01A-01-BS1.7fb47325-39cf-46b6-b5af-19a2a49a0965 | TCGA-CQ-A4CE-01A-01-TSA.A77CF515-6E29-476A-883A-74ED6F4DB34E
91 | C3N-00857-25 | TCGA-CQ-7065-01A-01-TS1.03f8ca03-5e3d-463a-a2e2-2ae6efef5dbe | TCGA-CV-7440-01A-01-TS1.8eaac76e-b129-4cf3-9edf-3a16bf492bfb
92 | C3N-00297-24 | TCGA-QK-AA3J-01A-01-TS1.61AD0210-CB2B-45B8-854E-CF62DF0F40CE | TCGA-CV-6952-01A-01-TS1.af70ffda-6df8-4637-84da-8ab420721e8a
93 | C3N-04152-23 | TCGA-CQ-5333-01A-01-BS1.5dd9ebf4-5240-4c28-8da4-5b97e2160cb7 | TCGA-BA-6871-01A-01-TS1.b2842566-d052-40d6-88ff-6e6334493f37
94 | C3N-00295-22 | TCGA-HL-7533-01A-01-BS1.4de1ccaa-1e10-409b-aabe-ce65ed8075f4 | TCGA-CV-7235-01A-01-BS1.ec9fa67e-7cad-4383-8de7-dc932ebac00a
95 | C3N-03011-23 | TCGA-CN-5365-01A-01-BS1.4e19279e-7061-4da4-ae99-99ae087219fa | TCGA-UF-A71D-01A-01-TSA.8DBAA353-2312-4E3C-8A1C-AFFCA71945A1
96 | C3N-03458-24 | TCGA-CV-6936-01A-01-BS1.d936e3e3-9f60-4f2f-b7ae-1afbad53c0a6 | TCGA-BA-6872-01A-01-BS1.a57b58a9-f300-48b3-bc88-522f6b6d92ca
97 | C3L-00999-26 | TCGA-CN-4723-01A-01-TS1.a711bf0c-ae9c-4993-994f-ba8569ad9c57 | TCGA-CV-7235-11A-01-TS1.d12de93f-04c8-4291-b73d-d2c3e9cd52c5
98 | C3L-00994-23 | TCGA-CV-6951-01A-01-TS1.3263b1e3-9e63-4146-ba1d-3175e2f735d4 | TCGA-CV-6956-11A-01-TS1.cedba2c2-0b4a-4b8b-82e5-927ef5a6c8d7
99 | C3N-01337-25 | TCGA-CV-7247-11A-01-TS1.e0205178-70e2-4354-bd8b-0081b25d4571 | TCGA-QK-A64Z-01A-01-TSA.98ADDFD7-8C88-4704-9C70-60106C5903E2
100 | C3N-03837-23 | TCGA-CN-4735-01A-01-BS1.3de44351-49cf-485a-87bf-0c684e1cb16a | TCGA-CV-5431-01A-01-BS1.7d815fd8-43d4-4d42-bfa4-cde11bcfcf66
101 | C3N-03849-23 | TCGA-CN-6989-01A-01-TS1.689111bf-1d7a-4771-86fa-fc1226bae246 | TCGA-CV-6952-01A-01-BS1.a26a3339-83d5-4153-82e8-05945a4b3e90
102 | C3L-00994-24 | TCGA-CV-7177-11A-01-TS1.57bcd3d6-df12-47ac-b99f-2371521661bf | TCGA-UF-A7JA-01A-01-TS1.7D60ADC6-DFAC-4D16-A175-0CF10321ED1B
103 | C3N-02714-23 | TCGA-MZ-A6I9-01A-01-TS1.83A1A06C-9D5E-4E7A-AC5E-59C50DB7051E | TCGA-CV-7245-01A-01-BS1.90f06679-0397-4688-8c75-b1855efa4bd1
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

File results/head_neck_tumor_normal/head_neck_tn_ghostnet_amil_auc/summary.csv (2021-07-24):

 | folds | test_auc | val_auc | test_acc | val_acc
0 | 0 | 0.974667239158437 | 1.0 | 0.9805194805194806 | 0.99375

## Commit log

2021-07-24 Add stls
    [condenser.stl, condenser_mount.stl, lcd_and_board_bottom.stl, lcd_and_board_top.stl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]
2021-07-24 Add phone_clam
    [bwh.csv, bwh_biopsy.csv, bwh_head_neck_microscopy_FFPE_tn.csv, bwh_head_neck_microscopy_FS_tn.csv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]
2021-07-25 Rm stuff
    [bwh_head_neck_microscopy_FFPE_tn.csv, bwh_head_neck_microscopy_FS_tn.csv, bwh_lung_microscopy_FFPE_ad_sq.csv, bwh_lung_microscopy_FFPE_tn.csv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]
2021-08-18 Add scad
    [lcd_and_board.scad, lcd_and_board_bottom.stl, lcd_and_board_bottom_part.stl, lcd_and_board_top.stl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]
